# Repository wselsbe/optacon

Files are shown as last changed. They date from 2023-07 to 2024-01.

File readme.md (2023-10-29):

# Optacon

This project aims to recreate the [Optacon](https://en.wikipedia.org/wiki/Optacon) (OPtical to TActile CONverter), a reading aid for the blind. The user moves a small camera module over a document to scan one letter at a time. The main module has a "tactile display": a 6x24 array of vibrating pins, so the user can feel the shape of the letter being scanned with their fingertip.

The vibrating pins are actuated by piezoelectric bimorphs, similar to those used in refreshable braille displays. The Optacon uses vibrating pins instead of static, and achieves a higher pin density: 1mm x 2mm versus 2.5mm x 2.5mm.
The following videos show the display in action. The piezo bimorphs actuate at around 250Hz, the motion appears slowed down by a stroboscopic led.

optacon pins (http://www.youtube.com/watch?v=8xHrjtj89DE)
optacon pins (http://www.youtube.com/watch?v=HoEaBOcu1ug)

The high density tactile display remains state of the art. Even now, 50 years later, there is no technology available that achieves the same high density while still remaining portable and battery powered.

# Recreating the tactile display
The smallest commercially available piezoelectric actuators are those meant for braille cells, and are 2.5mm wide. No piezo manufacturer wanted to try to create narrower actuators.

My solution is to start with an off the shelf 40mm x 20mm x 0.9mm actuator, and dice it into 20 individual parallel actuators with a [wafer dicing saw](https://www.eevblog.com/forum/reviews/micro-automation-m1006-dicing-saw). This uses a very precise air bearing spindle with a very thin (55 micron) diamond blade to cut through the piezoceramic. Because the blade is water cooled, the piezoceramic actuator remains below the curie temperature (about 150°C) and does not lose its polarisation.

## Holding and mounting the piezoceramic actuator for dicing
Holding the actuators during and after dicing proved challenging. Typically silicon wafers are mounted with [UV dicing tape](https://www.adwill-global.com/en/tape/dicing-d.html), but this tape is expensive.
Another potential solution is [heat release tape](https://www.nitto.com/eu/en/products/e_parts/electronic001/), where the adhesive softens at higher temperature (but still below the piezoceramic curie temperature), but this is similarly expensive.

I got some success by using [Crystalbond 509](https://www.aremco.com/mounting-adhesives/): by heating it to 74°C on a hotplate I could apply the adhesive to a glass disc, add the piezoceramic, and letting the adhesive cool down to harden. The disc is then held in place the the dicing saw's vacuum chuck. But transferring the diced actuators to a pcb, while still remaining parallel after dicing, proved to be too difficult. The Crystalbond 509 has to be released by using heat and a solvent (acetone), without affecting the second adhesive used to attach the piezoceramic reeds to the pcb.

The key proved to be in reversing the steps.

1. First populate the pcb and reflow solder as usual
2. Apply the conductive adhesive on the pcb actuator pads with a stencil. I'm using MG Chemicals [8331S](https://mgchemicals.com/products/adhesives/electrically-conductive-adhesives/electrically-conductive-paste/) 2-part or [9410](https://mgchemicals.com/products/adhesives/electrically-conductive-adhesives/conductive-adhesive/) 1-part silver epoxy.
3. Attach the piezoceramic and heat-cure the epoxy on a hot plate or in a reflow (toaster) oven. The above epoxies can cure below the curie temperature.
4. Mount the pcb to the glass disc with [Crystalbond 555-HMP](https://www.aremco.com/mounting-adhesives/). Although 555 has much lower tensile strength compared to 509, the larger surface area of the pcb is enough to keep it in place.
   The silver epoxy provides enough shear strengths to hold the individual actuators on one end. By applying the Crystalbond 555 on the underside of the piezoceramic through the slots in the pcb, the free ends of the diced piezoceramic reeds remain supported.
5. Dice the piezoceramic.
6. Crystalbond 555 is water soluble, any adhesive exposed to the water cooling from the dicing blade will be removed quickly while dicing. To detach the pcb from the glass disc it can be placed in a heated ultrasonic cleaner.

# Electronics

## Actuator board

The actuator board is designed around 2 components: a high voltage piezo driver, and high voltage shift registers .
All components are chosen for small size and low height, to keep the boards stackable. The tallest component is the inductor at 1.2mm. The passive components are 0603 for manual pick and place.

### Piezo Driver

The [TI DRV2665](https://www.ti.com/product/DRV2665) can output 100V with only an inductor and capacitor. It has an I2C interface and an analog input. 
Alternatives are [DRV2667](https://www.ti.com/product/DRV2667) (pin compatible) and [DRV8667](https://www.ti.com/product/DR8667) & [DRV2700](https://www.ti.com/product/DRV2700) (analog only)
The inductor [TDK VLS3012HBX-3R3M](https://product.tdk.com/en/search/inductor/inductor/smd/info?part_no=VLS3012HBX-3R3M) is chosen for low height, low resistance (150mΩ), and high current (2.37A temp rating).
The capacitor is rated for 200V.
TI has an [excel sheet](https://www.ti.com/tool/download/SLOR113) to help calculate the values for the inductor, capacitor, and feedback resistors.

To increase the efficiency the piezo driver is powered from VIN (battery or usb). The I2C lines are pulled up to VDD (3.3V), compatible down to 1.8V

The piezo driver has a differential output, which can drive piezos at 200V peak to peak. Because of the shift registers only one output (up to 100V) is used.
Without input the outputs float at half the boost voltage, ideally the external controller should make sure the input is pulled down.

The I2C and analog input pins are broken out to the FFC connector.

### Shift Registers

The [Microchip HV509](https://www.microchip.com/en-us/product/HV509) high voltage shift registers are used to address the individual piezo actuators. There are no real alternatives available in QFN or similar low height package.
The common BP pin is connected to the common bottom & top electrodes on the piezos. The individual outputs go to the center electrodes. There are 16 outputs per shift registers, 10 are used on each shift register, the other 6 are unused.
Diode D1 is needed to bias the output transistors to at least VDD before the high voltage is enabled.
The datasheet says the minimum voltage is 50V for the outputs to switch. In practice this does not look like a major issue: if the HV is a sine wave they might switch late, but will still pass through the lower voltage after switching. (Needs further testing)

Both shift registers are chained together, the SPI pins (clock, data in, data out) and Latch and Polarity are broken out to the FFC connector

## Motherboard

The motherboard is designed to drive several actuator boards (up to 6), a future revision will accept external input such as a camera to read printed letters.
It's based on an ESP32-S3-WROOM-1 module.
Currently the goal of the motherboard is to act as a controller and interface to the actuator boards. At first, the firmware should simply generate a sinewave and step through the individual actuators, as a test for the actuator boards.

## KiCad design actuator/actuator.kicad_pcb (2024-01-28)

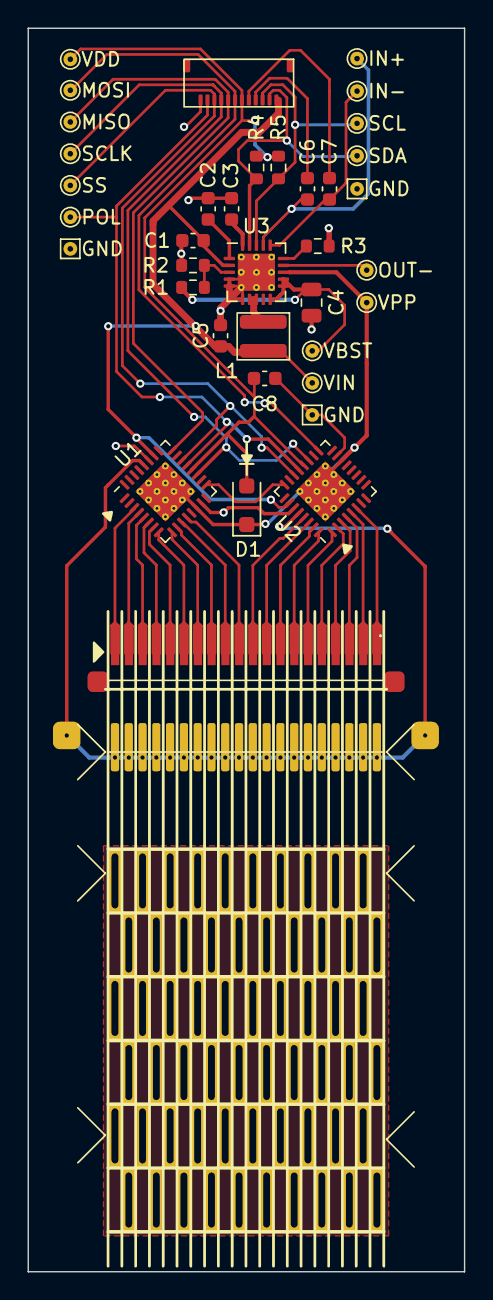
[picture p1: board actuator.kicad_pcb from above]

Board: 2 copper layers, 31.7 x 90.2 mm, 38 parts (0 on the bottom side), 44 nets.

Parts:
C1: 1 µF; C_0603_1608Metric
C2, C3, C6, C7, C8: 0.1 µF; C_0603_1608Metric
C4: 0.1 µF 150V+; C_0805_2012Metric
C5: 10 µF; C_0603_1608Metric
D1: D; D_SOD-123F
J1: Conn_01x12; Hirose_FH34SRJ-12S-0.5SH
J2: Conn_01x40_Socket; Hirose_FH34SRJ-40S-0.5SH
L1: 3.3 µH; TDK_VLS_3012
R1: 549k; R_0603_1608Metric
R2, R3: 6.98k; R_0603_1608Metric
R4, R5: 3.3k; R_0603_1608Metric
TP1, TP15: VDD; TestPoint_THTPad_D1.0mm_Drill0.5mm
TP2, TP2#2, TP2#3: TestPoint; TestPoint_THTPad_1.0x1.0mm_Drill0.5mm
TP3, TP4, TP5, TP6, TP7, TP8, TP9, TP10, TP11, TP12, TP13, TP14: TestPoint; TestPoint_THTPad_D1.0mm_Drill0.5mm
U1, U2: HV509; HVQFN-32-1EP_5x5mm_P0.5mm_EP3.1x3.1mm_ThermalVias
U3: DRV2665; Texas_S-PVQFN-N20_EP2.7x2.7mm_ThermalVias
piezo1: Conn_01x22; piezox20

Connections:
/IN+: C6.2, J1.9
/IN-: C7.1, J1.8
/MISO: J1.5, TP9.1, U1.24 (DOUT)
/MOSI: J1.6, TP8.1, U2.17 (DIN)
/OUT-: TP5.1, U3.14 (OUT-)
/POL: J1.2, TP13.1, U1.21 (~POL~), U2.21 (~POL~)
/PZT_Common: U1.28 (BP), U2.28 (BP), piezo1.21
/SCL: J1.10, R5.1, TP11.1, U3.18 (SCL)
/SCLK: J1.4, TP12.1, U1.19 (CLK), U2.19 (CLK)
/SDA: J1.11, R4.2, TP10.1, U3.19 (SDA)
/SS: J1.3, TP14.1, U1.22 (~LE~), U2.22 (~LE~)
/VBST: C4.1, R1.1, TP4.1, U3.10 (VBST), U3.11 (VBST), U3.12 (PVDD)
/VDD: C8.1, D1.2 (A), J1.7, R4.1, R5.2, TP1.1, U1.20 (VDD), U2.20 (VDD)
/VIN: C1.1, C5.1, J1.12, L1.2, TP15.1, U1.26 (VBIAS), U2.26 (VBIAS), U3.2 (VDD)
/VPP: D1.1 (K), TP3.1, U1.14 (VPP), U1.33 (VPP), U2.14 (VPP), U2.33 (VPP), U3.13 (OUT+)
/reed1: J2.39, J2.40, U1.3 (HVout10)
/reed2: J2.37, J2.38, U1.4 (HVout9)
/reed3: J2.35, J2.36, U1.5 (HVout8)
/reed4: J2.33, J2.34, U1.6 (HVout7)
/reed5: J2.31, J2.32, U1.7 (HVout6)
/reed6: J2.29, J2.30, U1.8 (HVout5)
/reed7: J2.27, J2.28, U1.9 (HVout4)
/reed8: J2.25, J2.26, U1.10 (HVout3)
/reed9: J2.23, J2.24, U1.11 (HVout2)
/reed10: J2.21, J2.22, U1.12 (HVout1)
/reed11: J2.19, J2.20, U2.29 (HVout16)
/reed12: J2.17, J2.18, U2.30 (HVout15)
/reed13: J2.15, J2.16, U2.31 (HVout14)
/reed14: J2.13, J2.14, U2.32 (HVout13)
/reed15: J2.11, J2.12, U2.1 (HVout12)
/reed16: J2.9, J2.10, U2.2 (HVout11)
/reed17: J2.7, J2.8, U2.3 (HVout10)
/reed18: J2.5, J2.6, U2.4 (HVout9)
/reed19: J2.3, J2.4, U2.5 (HVout8)
/reed20: J2.1, J2.2, U2.6 (HVout7)
GND: C1.2, C2.2, C3.2, C4.2, C5.2, C8.2, J1.1, R2.1, R3.2, TP2.1, TP2#2.1, TP2#3.1, U1.15 (GND), U1.27 (HVGND), U2.15 (GND), U2.27 (HVGND), U3.4 (GND), U3.5 (GND), U3.6 (GND), U3.21 (GND)
unnamed: L1.1, U3.7 (SW), U3.8 (SW)
unnamed: U1.17 (DIN), U2.24 (DOUT)
unnamed: R1.2, R2.2, U3.3 (FB)
unnamed: C6.1, TP6.1, U3.17 (IN+)
unnamed: C7.2, TP7.1, U3.16 (IN-)
unnamed: C3.1, U3.20 (REG)
unnamed: R3.1, U3.15 (REXT)
unnamed: C2.1, U3.1 (VPUMP)

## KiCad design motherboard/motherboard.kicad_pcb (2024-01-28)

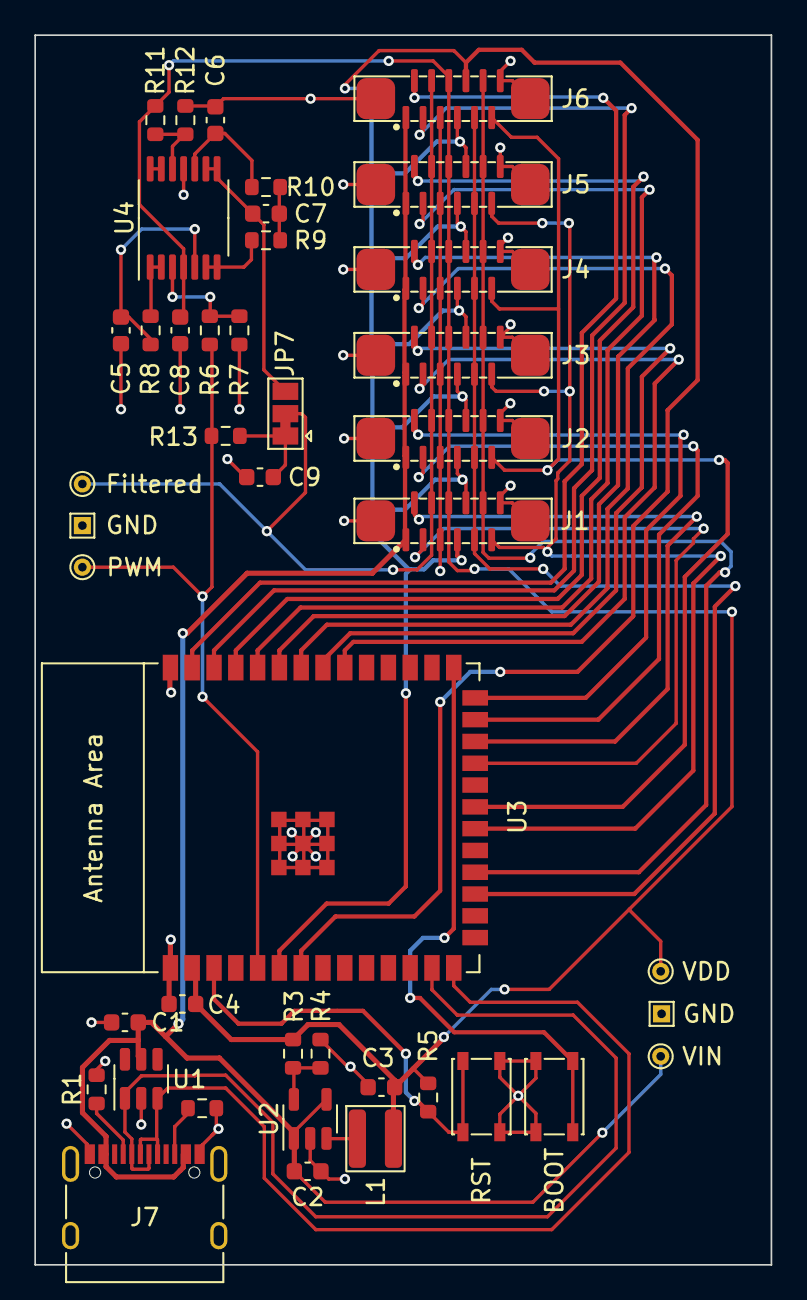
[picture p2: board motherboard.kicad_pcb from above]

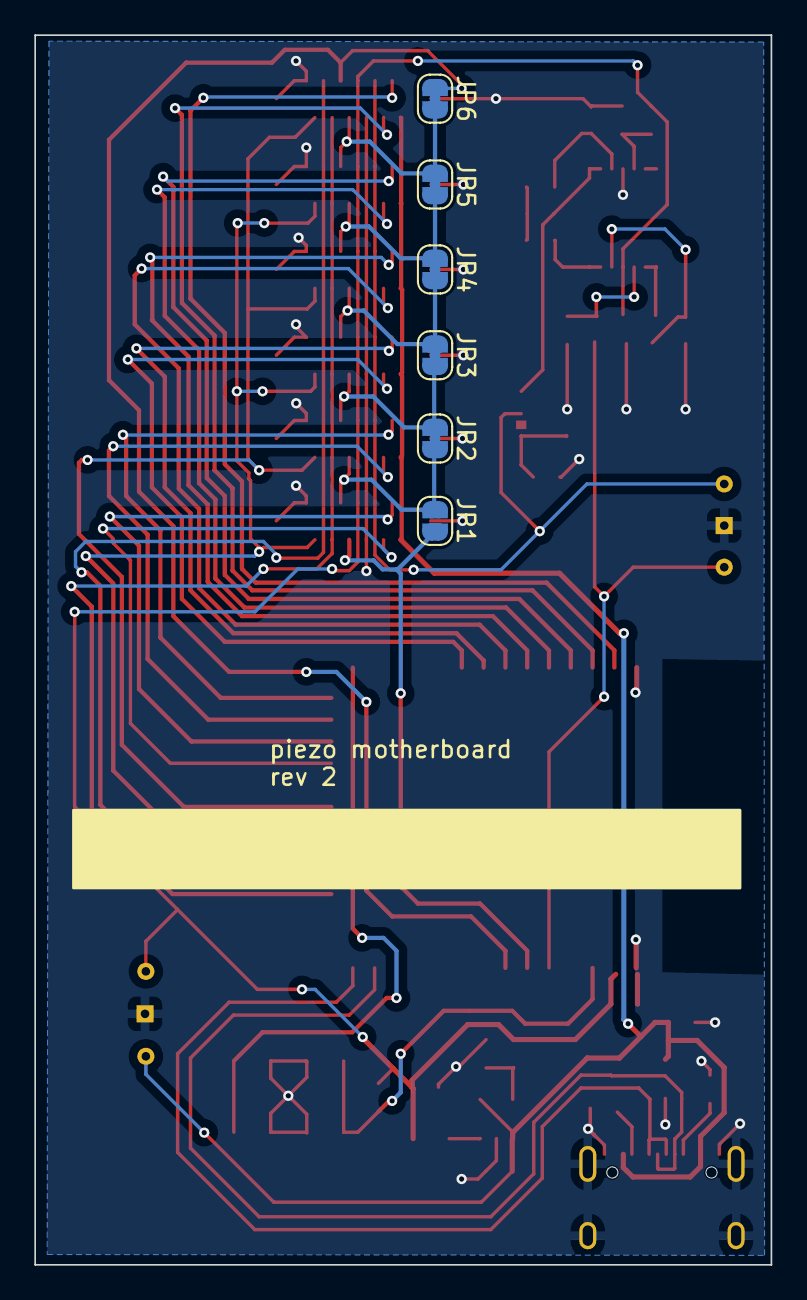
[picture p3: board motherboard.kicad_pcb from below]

Board: 2 copper layers, 42.9 x 71.7 mm, 49 parts (6 on the bottom side), 46 nets.

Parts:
C1, C4: C; C_0603_1608Metric
C2: 4.7µF; C_0603_1608Metric
C3: 10µF; C_0603_1608Metric
C5, C6, C8: 0.01µF; C_0603_1608Metric
C7: 0.047µF; C_0603_1608Metric
C9: 0.1µF; C_0603_1608Metric
J1, J2, J3, J4, J5, J6: Conn_01x12_MountingPin; Jushuo_AFC11-S12I
J7: USB_C_Receptacle_USB2.0; USB_C_Receptacle_XKB_U262-16XN-4BVC11
JP1: SolderJumper_2_Open; SolderJumper-2_P1.3mm_Open_RoundedPad1.0x1.5mm
JP2, JP3, JP4, JP5, JP6: SolderJumper_2_Bridged; SolderJumper-2_P1.3mm_Bridged_RoundedPad1.0x1.5mm
JP7: SolderJumper_3_Bridged12; SolderJumper-3_P1.3mm_Bridged12_Pad1.0x1.5mm
L1: 3.3µH; TDK_VLS_3012
R1, R2: 5.1K; R_0603_1608Metric
R3: 31.6k; R_0603_1608Metric
R4: 6.98k; R_0603_1608Metric
R5: R; R_0603_1608Metric
R6: 12.4K; R_0603_1608Metric
R7: 6.19K; R_0603_1608Metric
R8: 4.02K; R_0603_1608Metric
R9: 1.21K; R_0603_1608Metric
R10: 2.74K; R_0603_1608Metric
R11, R12: 100K; R_0603_1608Metric
R13: 390; R_0603_1608Metric
SW1: RST; SW_SPST_PTS810
SW2: BOOT; SW_SPST_PTS810
TP1, TP2, TP4, TP6: TestPoint; TestPoint_THTPad_D1.0mm_Drill0.5mm
TP3, TP5: TestPoint; TestPoint_THTPad_1.0x1.0mm_Drill0.5mm
U1: SRV05-4; SOT-23-6
U2: M3406-ADJ; SOT-23-5
U3: ESP32-S3-WROOM-1
U4: LM324; TSSOP-14_4.4x5mm_P0.65mm

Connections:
/D+: J7.A6 (D+), J7.B6 (D+), U1.3 (IO2), U3.14 (GPIO20/U1CTS/ADC2_CH9/CLK_OUT1/USB_D+)
/D-: J7.A7 (D-), J7.B7 (D-), U1.1 (IO1), U3.13 (GPIO19/U1RTS/ADC2_CH8/CLK_OUT2/USB_D-)
/IN+: J1.4, J2.4, J3.4, J4.4, J5.4, J6.4, JP7.2 (C), TP2.1
/MISO1: J1.8, J2.7, JP1.1 (A), JP2.2 (B)
/MISO2: J2.8, J3.7, JP2.1 (A), JP3.2 (B)
/MISO3: J3.8, J4.7, JP3.1 (A), JP4.2 (B)
/MISO4: J4.8, J5.7, JP4.1 (A), JP5.2 (B)
/MISO5: J5.8, J6.7, JP5.1 (A), JP6.2 (B)
/MISO6: J6.8, JP6.1 (A), U3.7 (GPIO7/TOUCH7/ADC1_CH6)
/MOSI1: J1.7, JP1.2 (B), U3.6 (GPIO6/TOUCH6/ADC1_CH5)
/POL1: J1.11, J3.11, J5.11, U3.20 (GPIO12/TOUCH12/ADC2_CH1/FSPICLK/FSPIIO6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)
/POL2: J2.11, J4.11, J6.11, U3.21 (GPIO13/TOUCH13/ADC2_CH2/FSPIQ/FSPIIO7/S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)
/PWM_OUT: R6.1, R13.1, TP1.1, U3.5 (GPIO5/TOUCH5/ADC1_CH4)
/SCL1: J1.3, U3.23 (GPIO21)
/SCL2: J2.3, U3.25 (GPIO48/SPICLK_N/SUBSPICLK_N_DIFF)
/SCL3: J3.3, U3.32 (MTCK/GPIO39/CLK_OUT3/SUBSPICS1)
/SCL4: J4.3, U3.34 (MTDI/GPIO41/CLK_OUT1)
/SCL5: J5.3, U3.36 (U0RXD/GPIO44/CLK_OUT2)
/SCL6: J6.3, U3.38 (GPIO2/TOUCH2/ADC1_CH1)
/SCLK: J1.9, J2.9, J3.9, J4.9, J5.9, J6.9, U3.17 (GPIO9/TOUCH9/ADC1_CH8/FSPIHD/SUBSPIHD)
/SDA1: J1.2, U3.24 (GPIO47/SPICLK_P/SUBSPICLK_P_DIFF)
/SDA2: J2.2, U3.26 (GPIO45)
/SDA3: J3.2, U3.33 (MTDO/GPIO40/CLK_OUT2)
/SDA4: J4.2, U3.35 (MTMS/GPIO42)
/SDA5: J5.2, U3.37 (U0TXD/GPIO43/CLK_OUT1)
/SDA6: J6.2, U3.39 (GPIO1/TOUCH1/ADC1_CH0)
/SS: J1.10, J2.10, J3.10, J4.10, J5.10, J6.10, U3.18 (GPIO10/TOUCH10/ADC1_CH9/FSPICS0/FSPIIO4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)
/VDD: C3.1, C4.1, C8.1, J1.6, J2.6, J3.6, J4.6, J5.6, J6.6, L1.2, R3.2, R5.1, R11.1, TP6.1, U3.2 (3V3), U4.4 (V+)
/VIN: C1.2, C2.1, J1.1, J2.1, J3.1, J4.1, J5.1, J6.1, J7.A4 (VBUS), J7.A9 (VBUS), J7.B4 (VBUS), J7.B9 (VBUS), TP4.1, U1.5 (VP), U2.1 (RUN), U2.4 (VIN)
GND: C1.1, C2.2, C3.2, C4.2, C5.2, C6.1, C8.2, C9.2, J1.5, J1.12, J1.MP (MountPin), J2.5, J2.12, J2.MP (MountPin), J3.5, J3.12, J3.MP (MountPin), J4.5, J4.12, J4.MP (MountPin), J5.5, J5.12, J5.MP (MountPin), J6.5, J6.12, J6.MP (MountPin), J7.A1 (GND), J7.A12 (GND), J7.B1 (GND), J7.B12 (GND), J7.S1 (SHIELD), R1.2, R2.2, R4.1, R7.2, R12.2, SW1.1, SW2.1, TP3.1, TP5.1, U1.2 (VN), U2.2 (GND), U3.1 (GND), U3.40 (GND), U3.41 (GND), U4.11 (V-)
unnamed: C7.1, R9.2, R10.1
unnamed: J7.A5 (CC1), R1.1
unnamed: J7.B5 (CC2), R2.1
unnamed: C9.1, JP7.1 (A), R13.2
unnamed: C7.2, JP7.3 (B), U4.8, U4.9 (-)
unnamed: R3.1, R4.2, U2.5 (FB)
unnamed: L1.1, U2.3 (SW)
unnamed: R5.2, SW1.2, U3.3 (EN)
unnamed: SW2.2, U3.27 (GPIO0/BOOT)
unnamed: R6.2, R7.1, U4.3 (+)
unnamed: R8.1, U4.1, U4.2 (-)
unnamed: C5.1, R8.2, U4.5 (+)
unnamed: R9.1, U4.6 (-), U4.7
unnamed: C6.2, R10.2, U4.10 (+)
unnamed: R11.2, R12.1, U4.12 (+)
unnamed: U4.13 (-), U4.14

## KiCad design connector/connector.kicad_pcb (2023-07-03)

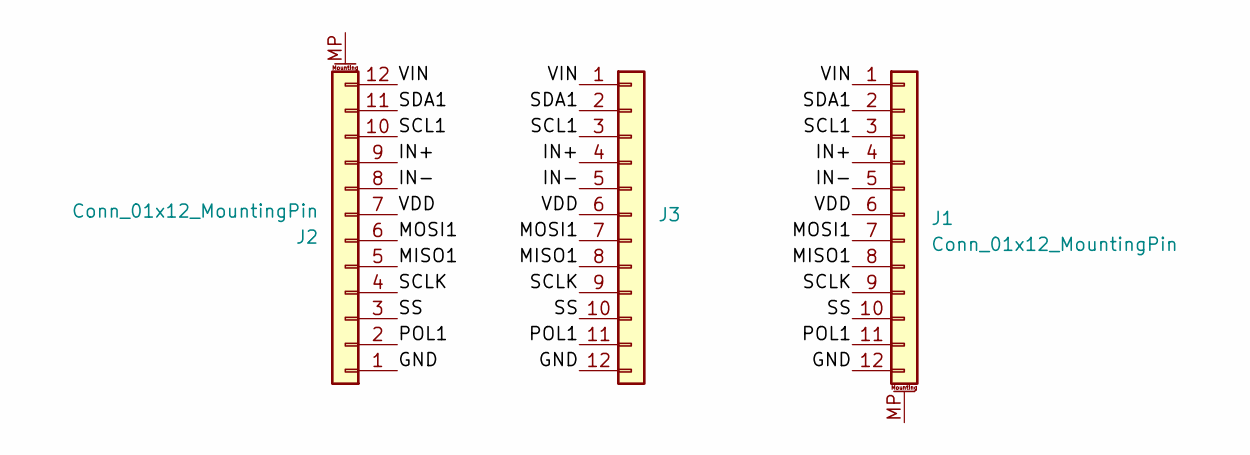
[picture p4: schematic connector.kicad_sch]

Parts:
J1, J2: Conn_01x12_MountingPin; Hirose_FH34SRJ-12S-0.5SH
J3: Conn_01x12; PinHeader_1x12_P2.54mm_Vertical

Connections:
/GND: J1.12, J2.1, J3.12
/IN+: J1.4, J2.9, J3.4
/IN-: J1.5, J2.8, J3.5
/MISO1: J1.8, J2.5, J3.8
/MOSI1: J1.7, J2.6, J3.7
/POL1: J1.11, J2.2, J3.11
/SCL1: J1.3, J2.10, J3.3
/SCLK: J1.9, J2.4, J3.9
/SDA1: J1.2, J2.11, J3.2
/SS: J1.10, J2.3, J3.10
/VDD: J1.6, J2.7, J3.6
/VIN: J1.1, J2.12, J3.1

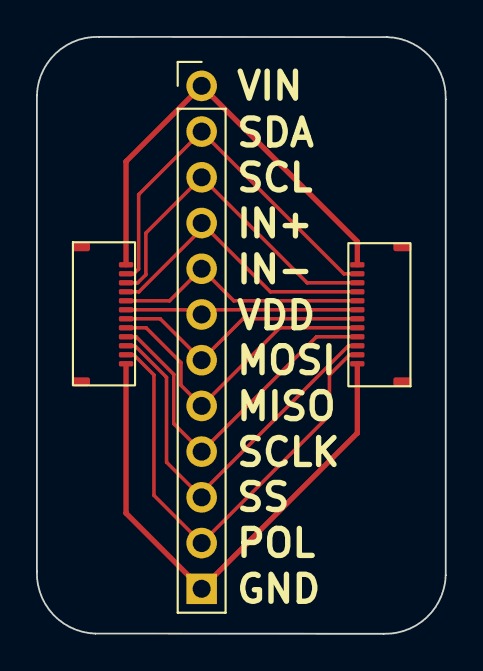
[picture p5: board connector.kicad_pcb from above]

Board: 2 copper layers, 22.7 x 33.2 mm, 3 parts (0 on the bottom side), 12 nets.

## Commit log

2022-04-19 driver pcb v1
    [optacon-B_Cu.gbl, optacon-B_Mask.gbs, optacon-B_Paste.gbp, optacon-B_Silkscreen.gbo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]
2022-04-20 wip: piezo footprint, drv2665 symbol
    [optacon.kicad_sch]
2022-04-20 drv2665 subsheet
    [hv_driver.kicad_sch, optacon.kicad_sch]
2022-04-25 schematic, footprints
    [hv_driver.kicad_sch, optacon.kicad_pcb, optacon.kicad_sch]
2022-06-08 bom update
    [optacon.kicad_pcb]
2022-06-13 driver board
    [hv_driver.kicad_sch, optacon-B_Cu.gbl, optacon-B_Paste.gbp, optacon-B_Silkscreen.gbo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]
2022-06-15 hole pattern for piezo vacuum
    [optacon.kicad_pcb]
2022-06-16 no paste (stencil) for piezo individual pads
    [optacon.kicad_pcb]
2022-08-21 WIP -added clearance for reeds center conductor header pins -removed jumper resistor & output cap on VBST -changed C4 high voltage cap to 0805, lower height above board -added C5 10µF cap at inductor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
    [hv_driver.kicad_sch, optacon.kicad_pcb, optacon.kicad_sch]
2022-08-21 add test points, mounting holes
    [optacon.kicad_pcb, optacon.kicad_sch]
2022-08-21 hierarchical sheet for shift registers
    [hv_driver.kicad_sch, optacon.kicad_pcb, optacon.kicad_sch, optacon.step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]
2022-11-02 move vias out of pad ; fix ground plane under hv528
    [optacon.kicad_pcb]
2022-11-05 thermal vias for HV509/HV528
    [optacon.kicad_pcb, optacon.kicad_sch]
2022-11-07 test points
    [optacon.kicad_pcb, optacon.kicad_sch, shift_registers.kicad_sch]
2022-11-08 align test points
    [optacon.kicad_pcb]
2022-11-15 pcb + stencils ordered from pcbgogo
    [hv_driver.kicad_sch, optacon-B_Cu.gbl, optacon-B_Mask.gbs, optacon-B_Paste.gbp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]
2023-06-11 remove VBIAS, EN, REG rename & reorder nets for i2c, spi add IN- next to IN+ (AIN) add SMD FPC connector for piezo use BP instead of HVOUTs for piezo_common
    [hv_driver.kicad_sch, optacon.kicad_pcb, optacon.kicad_sch]
2023-06-12 J2 (mounting) pads no paste
    [optacon.kicad_pcb, optacon.kicad_sch]
2023-06-13 separate VIN and VDD
    [hv_driver.kicad_sch, optacon.kicad_pcb, optacon.kicad_sch]
2023-06-13 realign test points
    [optacon.kicad_pcb]
2023-06-13 move SDA trace around R4, R5
    [optacon.kicad_pcb]
2023-06-25 work in progress: reorder project files
    [logic_supply.kicad_sch, microcontroller.kicad_sch, optacon.kicad_pcb, psu.kicad_pcb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]
2023-06-25 wip: move files, common symbols+footprints
    [actuator.kicad_pcb, actuator.kicad_sch, hv_driver.kicad_sch, logic_supply.kicad_sch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]
2023-06-27 motherboard basics routed
    [microcontroller.kicad_sch, motherboard.kicad_pcb, motherboard.kicad_sch]
2023-06-27 reroute motherboard: no traces under antenna
    [logic_supply.kicad_sch, microcontroller.kicad_sch, motherboard.kicad_pcb, motherboard.kicad_sch]
2023-06-28 fpc connector mounting points
    [motherboard.kicad_pcb, motherboard.kicad_sch]
2023-07-03 actuator: add capacitor for vdd, no exposed copper on backside
    [actuator.kicad_pcb, actuator.kicad_sch, hv_driver.kicad_sch, shift_registers.kicad_sch]
2023-07-03 connector: breakout board for 12-pin fpc
    [connector.kicad_pcb, connector.kicad_sch]
2023-07-03 motherboard: buttons silkscreen
    [motherboard.kicad_pcb]
2023-07-03 export: pcbs + stencils ordered from pcbgogo
    [actuator_panel-B_Cu.gbr, actuator_panel-B_Mask.gbr, actuator_panel-B_Paste.gbr, actuator_panel-B_Silkscreen.gbr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]
2023-07-17 actuator ibom
    [actuator.kicad_pcb, shift_registers.kicad_sch]
2023-08-01 move piezo smd connector, rework pads & adhesive
    [actuator.kicad_pcb, actuator.kicad_sch]
2023-08-01 Quick relayout of motherboard - rotate ESP32, move supporting parts to bottom edge, reroute traces
    [motherboard.kicad_pcb]
2023-08-02 rev3.1 gerbers
    [actuator.kicad_pcb, actuator_panel-B_Cu.gbr, actuator_panel-B_Mask.gbr, actuator_panel-B_Paste.gbr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]
2023-10-24 restore slots under actuators (fix #5)
2023-10-24 move up ffc connector (fix #1)
    [actuator.kicad_pcb]
2024-01-22 motherboard low pass filter
    [low pass filter.kicad_sch, motherboard.kicad_pcb, motherboard.kicad_sch]
2024-01-22 actuator move testpoints to subsheets
    [actuator.kicad_pcb, actuator.kicad_sch, hv_driver.kicad_sch, shift_registers.kicad_sch]
2024-01-28 motherboard add test points
    [logic_supply.kicad_sch, low pass filter.kicad_sch, motherboard.kicad_pcb]
2024-01-28 add 1st order low pass filter, with solder jumper
    [logic_supply.kicad_sch, low pass filter.kicad_sch, motherboard.kicad_pcb]
2024-01-28 add/update revision texts
    [actuator.kicad_pcb, motherboard.kicad_pcb]
